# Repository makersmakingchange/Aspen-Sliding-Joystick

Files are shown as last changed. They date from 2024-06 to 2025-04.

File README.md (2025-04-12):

# Aspen Sliding Joystick
The Aspen Sliding Joystick is a small, proportional joystick that has a sliding motion and can be used for adaptive gaming or computer access with a suitable adapter. It has a small range of motion of ±2mm and requires approximately 115 grams-force to fully deflect. It is low profile, with a height of 1.9 cm with the standard topper. This joystick has interchangeable toppers, an optional hand support, and optional mount adapters. The Aspen Sliding Joystick has the same joystick mechanism as the Birch Sliding USB Joystick, but is the analog version. 

The Aspen Joystick has a cable with a 3.5 mm TRRS audio plug (i.e., headphone jack). It is compatible with the [Forest Joystick Mouse Hub](https://www.makersmakingchange.com/s/product/forest-joystick-mouse-hub/01tJR000000E4bdYAC), the Sony PlayStation Access Controller, or the X1 or X2 analog input ports on the Microsoft Xbox Adaptive controller.

The device is comprised of off-the-shelf electronics and 3D-printed parts. The overall cost of materials for a single build is about $20 ($12 for the materials and $8 for shipping).

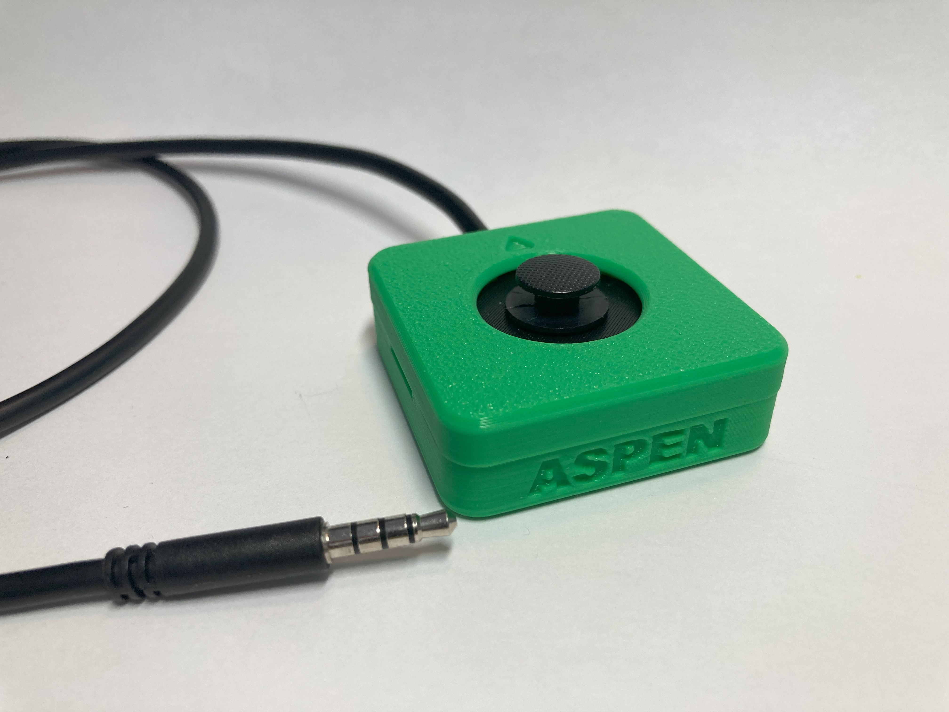
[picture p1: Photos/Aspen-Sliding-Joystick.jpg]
Picture of the Aspen Sliding Joystick, it is small and green and has ASPEN written on the front. The black cable comes out the back of the joystick and wraps around to show the jack on the end.


The Aspen Sliding Joystick can also be used with optional mount adapters to allow for use with a 1/4-20" camera mount or RAM mount systems. There is also an optional 3D-printed hand support. Below, pictured from left to  right are the Camera Mount Adapter, the RAM B Mount Adapter, and the Aspen Hand Support. 

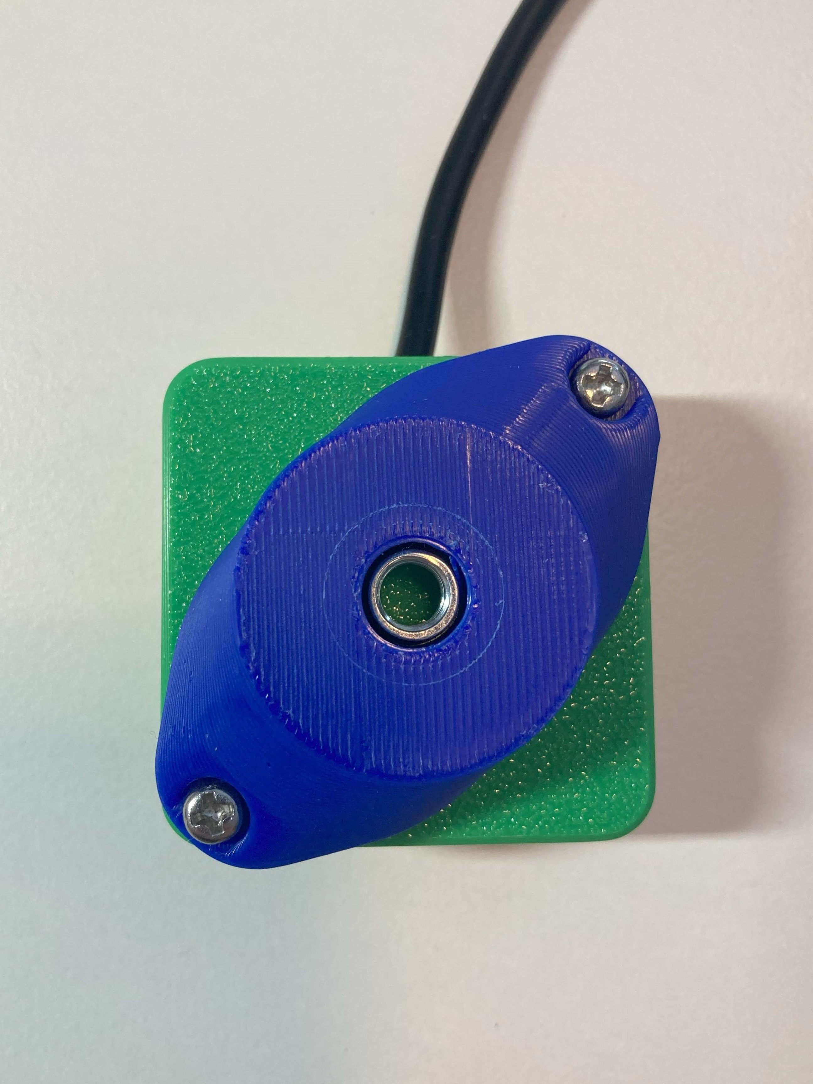
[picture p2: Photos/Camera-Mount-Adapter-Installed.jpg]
Picture of the back of a green Aspen Sliding Joystick with a blue camera mount adapter screwed into it. A black cable comes out the back of the joystick and goes out of frame.
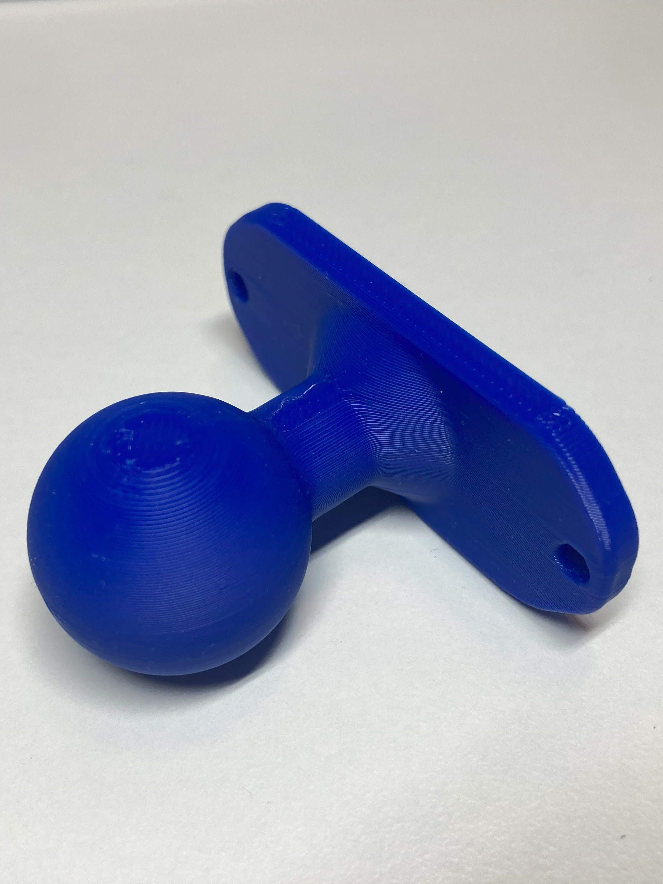
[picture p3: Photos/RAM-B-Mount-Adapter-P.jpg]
Picture of a blue RAM B mount adapter on a white background.
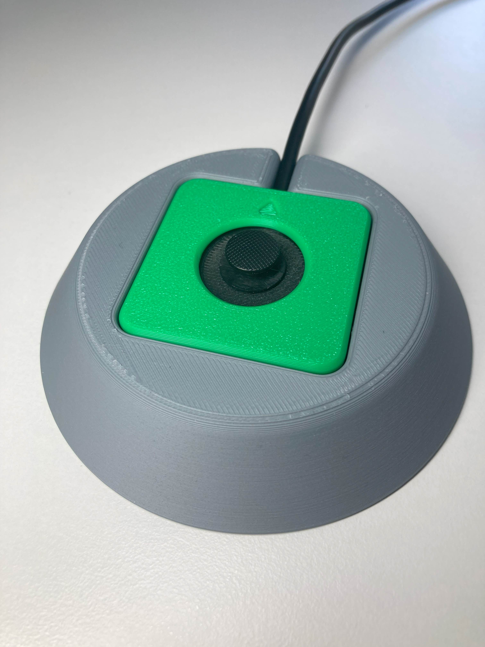
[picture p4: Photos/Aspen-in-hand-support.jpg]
Picture of a green Aspen Sliding Joystick in a grey circular hand support.A black cable comes out the back of the joystick and goes out of frame.
  

## More info at
- [Makers Making Change Assistive Device Library Listing](https://www.makersmakingchange.com/s/product/aspen-sliding-joystick/01tJR000004sCptYAE)

## OpenAT Joysticks
This design is part of the [OpenAT Joystick Project](https://github.com/makersmakingchange/OpenAT-Joysticks), a collection of open source designs for digital access and adapted gaming.  

## How to Obtain a Aspen Sliding Joystick
### 1. Do it Yourself (DIY) or Do it Together (DIT)

This is an open-source assistive technology, so anyone is free to build it. All of the files and instructions required to build the Aspen Sliding Joystick are contained within this repository. Refer to the Maker Guide below.

### 2. Request a build of this device

If you would like to obtain an Aspen Sliding Joystick, you may submit a build request through the [MMC Library Page](https://www.makersmakingchange.com/s/product/aspen-sliding-joystick/01tJR000004sCptYAE). The requestor is responsible for the cost of materials and any shipping.

### 3. How to build this device for someone else

If you have the skills and equipment to build this device, and would like to donate your time to create the joystick for someone who needs it, visit the [MMC Maker Wanted](https://makersmakingchange.com/maker-wanted/) section.

## Getting Started

### 1. Verify Joystick Type
The Aspen Sliding Joystick is an analog joystick that uses a [TRRS](https://www.sparkfun.com/products/11580) lead to connect to an existing gamepad such as the [Forest Joystick Mouse Hub](https://www.makersmakingchange.com/s/product/forest-joystick-mouse-hub/01tJR000000E4bdYAC), the Microsoft Xbox Adaptive Controller (XAC), or the Sony PlayStation Access Controller. Verify that this is the type of joystick the user would like. 

If they want a USB joystick with the same sliding motion instead, they should be directed to the Birch Sliding USB Joystick.

<!---
Other available joysticks can be found through the [Joystick Selection Guide](https://makersmakingchange.com/resource/analog-joystick-selection-guide/)
--->

### 2. Read through the Maker Guide

The [Maker Guide](/Documentation/Aspen_Joystick_Maker_Guide.pdf) contains all the necessary information to build the device.

### 3. Read the Makers Checklist

Use the Makers Checklist in the [Maker Guide](/Documentation/Aspen_Joystick_Maker_Guide.pdf) to confirm details and customization options with the user.

### 4. Order the Off-The-Shelf Components

The [Bill of Materials](/Documentation/Aspen_Joystick_BOM.csv) lists all of the parts and components required to build the Aspen Sliding Joystick. 

### 5. Print the 3D Printable components

Print the components needed for the Aspen Sliding Joystick. Make sure to ask the user if they would like any of the optional prints such as toppers, mount adapters, or the hand support. 

All of the files and individual print files can be in the [/Build_Files/3D_Print_Files](/Build_Files/3D_Print_Files/) folder.

### 6. Assemble the Aspen Sliding Joystick

Reference the Assembly Guide section in the [Maker Guide](/Documentation/Aspen_Joystick_Maker_Guide.pdf) for the tools and steps required to build the device.

## Files
### Documentation
| Document             | Version | Link 	| 
|----------------------|---------|------------------------------------------------------------------------------------------|
| Design Rationale     | 1.0     | [Aspen_Joystick_Design_Rationale](/Documentation/Aspen_Joystick_Design_Rationale.pdf)    |
| Maker Checklist      | 1.0     | [Aspen_Joystick_Maker_Guide](/Documentation/Aspen_Joystick_Maker_Guide.pdf)           	| 
| Bill of Materials    | 1.0     | [Aspen_Joystick_Bill_of_Materials](/Documentation/Aspen_Joystick_BOM.csv)     		    |     
| User Guide           | 1.0     | [Aspen_Joystick_User_Guide](/Documentation/Aspen_Joystick_User_Guide.pdf)    	        | 
| Changelog            | 1.0     | [CHANGES](/CHANGES.txt)     			| 

### Design Files
 - [CAD Files](/Design_Files)

### Build Files
 - [3D Print Files](/Build_Files/3D_Print_Files)

## License

Everything needed or used to design, make, test, or prepare the Aspen Sliding Joystick is licensed under the CERN 2.0 Weakly Reciprocal license <https://ohwr.org/project/cernohl/wikis/Documents/CERN-OHL-version-2> (CERN-OHL-W).

Accompanying material such as instruction manuals, videos, and other copyrightable works that are useful but not necessary to design, make, test, or prepare the Aspen Sliding Joystick are published under a Creative Commons Attribution-ShareAlike 4.0 license <https://creativecommons.org/licenses/by-sa/4.0/> (CC BY-SA 4.0).

## Attribution

Contributors
- Josie Versloot, Neil Squire. Design and documentation. 

The documentation template was created by Makers Making Change / Neil Squire and is used under a CC BY-SA 4.0 license. It is available at the following link: https://github.com/makersmakingchange/OpenAT-Template

---

<!-- ABOUT MMC START -->
## About Makers Making Change
[Makers Making Change Logo](https://www.makersmakingchange.com/)

Makers Making Change is a program of [Neil Squire](https://www.neilsquire.ca/), a Canadian non-profit that uses technology, knowledge, and passion to empower people with disabilities.

Makers Making Change leverages the capacity of community based Makers, Disability Professionals and Volunteers to develop and deliver affordable Open Source Assistive Technologies.

 - Website: [www.MakersMakingChange.com](https://www.makersmakingchange.com/)
 - GitHub: [makersmakingchange](https://github.com/makersmakingchange)
 - Bluesky: [@makersmakingchange.bsky.social](https://bsky.app/profile/makersmakingchange.bsky.social)
 - Instagram: [@makersmakingchange](https://www.instagram.com/makersmakingchange)
 - Facebook: [makersmakechange](https://www.facebook.com/makersmakechange)
 - LinkedIn: [Neil Squire Society](https://www.linkedin.com/company/neil-squire-society/)
 - Thingiverse: [makersmakingchange](https://www.thingiverse.com/makersmakingchange/about)
 - Printables: [MakersMakingChange](https://www.printables.com/@MakersMakingChange)

### Contact Us
For technical questions, to get involved, or to share your experience we encourage you to [visit our website](https://www.makersmakingchange.com/) or [contact us](https://www.makersmakingchange.com/s/contact).
<!-- ABOUT MMC END -->

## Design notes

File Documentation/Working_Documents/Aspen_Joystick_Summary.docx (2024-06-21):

This document is intended to be a summary of a device to make it easier to add to the website.

# Product Information

## Product Name

Aspen Sliding Joystick

## Device Category

Mark any relevant categories with an “X”:

| Adapted Toys
| Aids for Daily Living (ADL)
| Assistive Switches
| Communication Aids (AAC)
X | Computer Access
| Environmental Controls
X | Gaming
| Keyguard
| Kits
| LipSyncs
| Mounting
X | Recreation and Leisure
| Seating and Positioning
| Switch Interfaces
| Writing Aids

## User Value Statement

If you're looking for a small, analog joystick with a very small range of motion we'd like to point you to the Aspen Sliding Joystick.

## Designer

Makers Making Change

# Device Info

## Overview

The Aspen Sliding Joystick is a small analog joystick that moves in a sliding motion instead of the typical pivoting motion of a joystick or thumbstick. It can be used for adapted gaming or computer access with a suitable adaptive controller or hub. This joystick can be used directly with the Xbox Adaptive Controller (https://www.xbox.com/en-CA/accessories/controllers/xbox-adaptive-controller) or PlayStation Access Controller, or can be combined with the Forest Joystick Mouse Hub (https://github.com/makersmakingchange/Forest-Joystick-Mouse-Hub) and some assistive switches to create a USB HID Mouse or USB HID Gamepad.

The PSP-style game controller sliding thumbstick joystick has a range of motion of ±2 mm and requires approximately 115 grams-force to fully deflect. A range of toppers and mounting adapters are available for this joystick. The Aspen Sliding Joystick has the same joystick mechanism as the Birch Sliding USB Joystick, but is the analog version.

## Disability Type

Select one or more disability types and mark with an “X”:

X | Agility / Dexterity
| Arthritis
| Cognitive
| Hearing
| Mobility
| Mobility
| Pain
X | SCI
| Vision
| Other

## Disability Type Description

This device is designed for users with a very small range of motion that need an external joystick for adaptive gaming or computer access.

## How To Use

To use the Aspen Sliding USB Joystick, first position the joystick for the user, mounting if needed. Then, plug in the 3.5 mm cable to the host device, such as the Forest Hub, Xbox Adaptive Controller, or PlayStation Access Controller.

For full instructions, please refer to the User Guide (https://github.com/makersmakingchange/Aspen-Sliding-Joystick/blob/main/Documentation/Aspen_Joystick_User_Guide.pdf).

## Estimated Cost

The estimated material cost of the device for a single build:

| $0 - $10
X | $11 - $25
| $26 - $50
| $51 - $100
| $101 - $250
| $250+

## Attribution

Designed by Neil Squire Society / Makers Making Change

Contributors

- Josie Versloot, Neil Squire. Design and documentation.

The documentation template was created by Makers Making Change / Neil Squire and is used under a CC BY-SA 4.0 license. It is available at the following link: https://github.com/makersmakingchange/OpenAT-Template

# Maker Info

## Project Skills

Mark the required project skills with an “X”:

X | 3D Printing
| Custom PCB
| Electronics
| Laser Cutting
| Mechanics
| Software
X | Soldering
| Woodworking
| Other

## Skills Description

This is an intermediate build requiring 3D printing, and soldering electronic components.

## Tools Needed

X | 3D Printer
X | Common Hand Tools
| Common Power Tools
| Laser Cutter
X | Soldering Iron
| Specialized Tooling

## Print time (hrs)

1.5

## Assembly time (hrs)

1.0

## Build Instructions

This build consists of 4 off the shelf components and a 3D printed enclosure. The commercial parts are soldered together and then assembled into the 3D printed enclosure using snap fits.

Detailed step-by-step instructions are available in the Maker Guide (https://github.com/makersmakingchange/Aspen-Sliding-Joystick/blob/main/Documentation/Aspen_Joystick_Maker_Guide.pdf).

## Download Link

https://github.com/makersmakingchange/Aspen-Sliding-Joystick/archive/refs/heads/main.zip

## Project Link

https://github.com/makersmakingchange/Aspen-Sliding-Joystick

# License

## License

This repository describes Open Hardware:

- Everything needed or used to design, make, test, or prepare the Aspen Sliding Joystick is licensed under the CERN 2.0 Weakly Reciprocal license (CERN-OHL-W v2) or later (https://cern.ch/cern-ohl) .
- Accompanying material such as instruction manuals, videos, and other copyrightable works that are useful but not necessary to design, make, test, or prepare the Aspen Sliding Joystick are published under a Creative Commons Attribution-ShareAlike 4.0 license (CC BY-SA 4.0) (https://creativecommons.org/licenses/by-sa/4.0/) .

You may redistribute and modify this documentation and make products using it under the terms of the CERN-OHL-W v2 (https://cern.ch/cern-ohl). This documentation is distributed WITHOUT ANY EXPRESS OR IMPLIED WARRANTY, INCLUDING OF MERCHANTABILITY, SATISFACTORY QUALITY AND FITNESS FOR A PARTICULAR PURPOSE. Please see the CERN-OHL-W v2 for applicable conditions.

© 2024 by Neil Squire. This work is licensed under the CC BY SA 4.0 License: http://creativecommons.org/licenses/by-sa/4.0 Page 1 of 2

V1.0 | JUNE 2024 Aspen Sliding Joystick Summary

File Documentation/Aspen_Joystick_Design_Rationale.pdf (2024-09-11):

V1.1 | SEPTEMBER 2024

## Aspen Sliding Joystick

## DESIGN RATIONALE

© 2024 by Neil Squire Society. (https://www.neilsquire.ca/)

This work is licensed under the CC BY SA 4.0 License: http://creativecommons.org/licenses/by-sa/4.0
Files available at https://github.com/makersmakingchange/Aspen-Sliding-Joystick | Page 1 of 23

### Introduction

With adaptive gaming joysticks that are compatible with both PC and XAC being difficult to source globally, MMC aims to provide a cost-effective, open source customizable joysticks using easy to source components. Unlike commercial versions, these devices will be designed for Maker assembly with all the digital files necessary to customize key components easily.

The Aspen Sliding Joystick is the smaller, analog, version of the Birch Sliding Joystick. Previously, the analog and USB versions of the sliding joystick were made using the same enclosure and were named the Birch Mini Joystick-A and Birch Mini Joystick-U. The analog version was a lot bigger than it needed to be, and hardware increased the cost, so the Aspen Sliding Joystick came to be.

The intended user is someone with a very small range of motion, or for someone who prefers a joystick with a sliding motion.

### Research

### Commercially Available Options

1. Inclusive Inc Slider Joystick (https://inclusiveinc.org/en-ca/products/slider-joystick)

Cost (without shipping): $208.00 CAD

Dimensions: Not given

Features:

- Made to work with Versatilty v3 (https://inclusiveinc.org/products/v3) with circular 8 pin analog joystick port
- Low profile (no dimensions indicated)
- Mounting slots on the side

## DESIGN RATIONALE

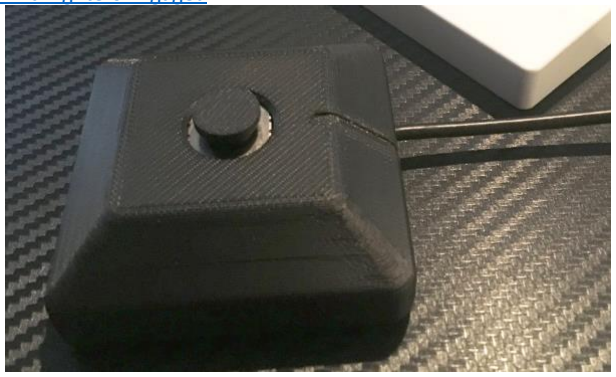
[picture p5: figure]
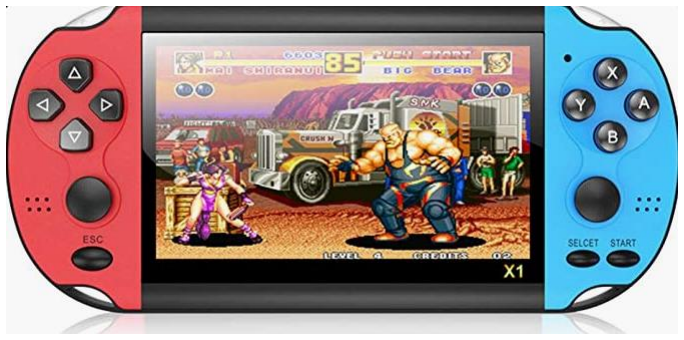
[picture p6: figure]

Files available at https://github.com/makersmakingchange/Aspen-Sliding-Joystick | Page 2 of 23
2. MINISTIX-SL Warfighters Engaged (https://warfighterengaged.org/shop/ministix-s)

Cost (without shipping): $45.00 USD

Dimensions: Not given

Features:

- ¼-20 threaded hole on the back for mounting.
- 3.5 mm integrated cable
3. Amazon - PSP type device (https://www.amazon.ca/ZADAI-4-3-inch-Handheld-Console-Portable/dp/B095WXBYSQ?hvadid=582450275413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)
*This example is more of how the device has sliding joysticks incorporated as the PlayStation PSP or Vita are no longer available.

Cost (without shipping): $99.99 CAD

Dimensions: N/A

## DESIGN RATIONALE

Files available at https://github.com/makersmakingchange/Aspen-Sliding-Joystick | Page 3 of 23

Features:

- Uses two sliding joysticks in a handheld set up for two handed gaming.
- Replaces the PlayStation PSP and Vita which popularized sliding joysticks in gaming

### Open Source Options:

1. Slider Joystick MKIII - Ron Nelson (https://www.etsy.com/ca/listing/1191918398/slider-joystick-mkiii-for-xbox-adaptive?click_sum=caf10b44&crt=1)
a. Github: https://github.com/nelsonii/JoystickEnclosures/tree/main/Slider

Cost (without shipping):

- Sold for: $77.86 CAD
Dimensions: N/A

Features:

- USB connection (intended for XAC)
- LED indicator light
- PC compatibility and also used with JoyToKEy (https://joytokey.net/en/)
- Features 3D printed disk topper with rubber 1.5 inch inserts for increased surface area

## DESIGN RATIONALE

Files available at https://github.com/makersmakingchange/Aspen-Sliding-Joystick | Page 4 of 23

### Requirements

### Goals

G01 | Minimize the size of the enclosure.
G02 | Minimize the cost.

### Functional Requirements

F01 | The joystick design must have a 3.5 mm TRRS analog output.
F02 | The joystick must be compatible with the Xbox Adaptive Controller and Forest Hub.
F03 | The joystick shall be designed to be used by either hand.
F04 | Joystick must remain stable while in use.
F05 | Joystick design must reduce possibilities of damage to electronic components of device by reducing openings to internal components.

### Constraints

C01 | Joystick must be maker manufacturable. (i.e. made with common tools and materials)
C02 | Design must be considered low profile and the total height must not exceed that of the Birch Mini Joystick, which is 24 mm.
C03 | The total maker cost must be less than or equal to that of the Birch Mini Joystick-A, which was $38.76.
C04 | The joystick must include two M3 nuts 50 mm apart to be compatible with the Joystick Mount Adapters.

## DESIGN RATIONALE

Files available at https://github.com/makersmakingchange/Aspen-Sliding-Joystick | Page 5 of 23

### Ideation

### Key Features

Joystick Unit
For this design, the same joystick element will be used as the Birch Joystick, the small sliding thumbstick from Adafruit. It is called the “Mini 2-Axis Analog Thumbstick” on the Adafruit website, product number 2765.

Snap fit to secure joystick
In this design, one of the goals was to minimize the cost, and decrease the cost compared to the Birch Mini Joystick-A design. One of the main costs when doing a single build of this previous design was fasteners, the M2 screws needed to fit through the joystick breakout board were difficult to find in small quantities and had to be bought in a pack of 1000. To eliminate this, a snap fit would be explored to secure the joystick.

Snap fit enclosure
To further reduce costs, a snap fit enclosure will also be explored, in the aim to eliminate the cost of fasteners altogether.

Mounting
To allow for different mounting options, captive M3 nuts compatible with the OpenAT Joystick Mount Adapters will be included. These must be 50 mm apart, and will allow different mount adapters to be attached to the bottom of the joystick, including a ¼-20” camera mount.

### Conceptual Design

The size of the joystick unit is quite small, and therefore the required dimensions of the captive nuts for the mount adapter will be the main constraint when it comes to size. There are two main ways the captive nuts can be oriented, vertically, horizontally, or diagonally. To allow users to place other devices close to the joystick, the vertical orientation is preferred over horizontal, so the vertical and diagonal mount adapter options were explored further.

### Concept 1 : Vertical Mount Adapter

With the mount adapter nuts in a vertical orientation, this creates a very long and skinny joystick when trying to minimize size. For aesthetics and stability, more width could be added to this design if needed. The dimensions of this concept would be approximately 35 mm x 60 mm at this minimum size.

## DESIGN RATIONALE

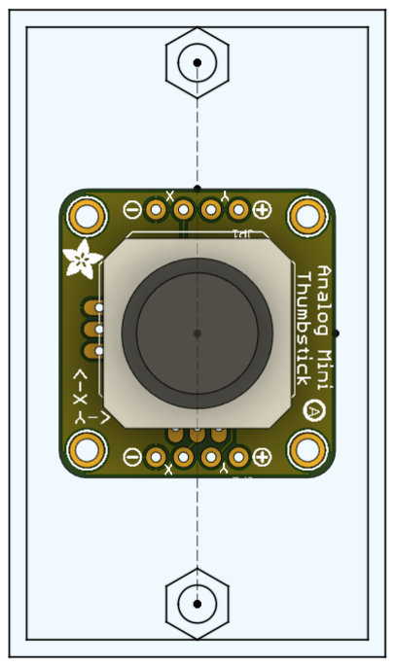
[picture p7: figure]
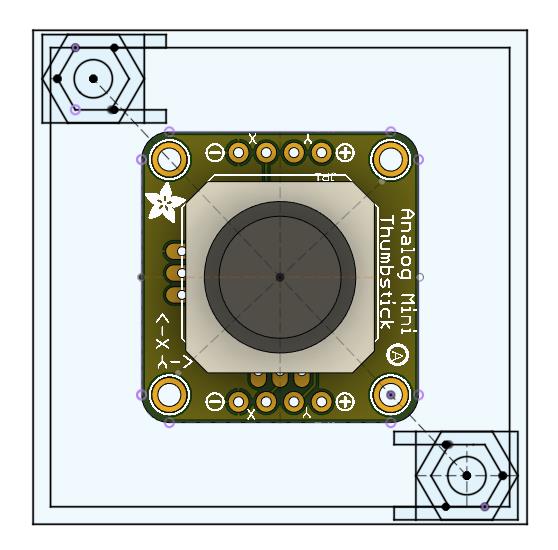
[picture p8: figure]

Files available at https://github.com/makersmakingchange/Aspen-Sliding-Joystick | Page 6 of 23

### Concept 2 : Diagonal Mount Adapter

With the mount adapter nuts in a diagonal orientation, the joystick would be more square. At these minimum dimensions, the size of this concept would be around 45 mm x 45 mm.

### Concept Selection

The concept with the diagonal mount adapter nuts was chosen, due to its more square geometry, which would be more stable while in use, is more aesthetically pleasing, and has a smaller overall footprint.

## DESIGN RATIONALE

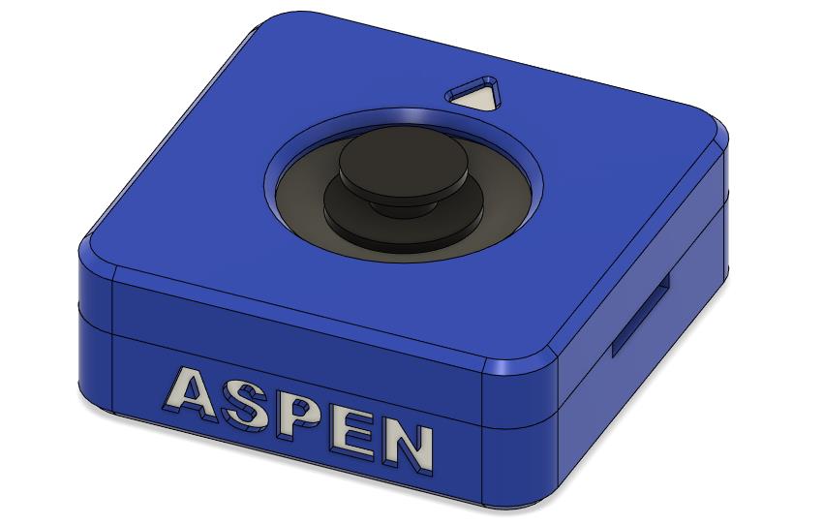
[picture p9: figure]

Files available at https://github.com/makersmakingchange/Aspen-Sliding-Joystick | Page 7 of 23

### Detailed Design

### Overview

The Aspen Sliding Joystick is small and compact, with a snap fit enclosure. Below the overall design is pictured:

Components
The components used in this design are the sliding joystick module and breakout board, a TRRS stereo audio cable, and 2 hex nuts. The parts are all listed in the following table, and more information including prices can be found in the Bill Of Materials (BOM).
Part Name | QTY | Link
Mini 2-Axis Analog Thumbstick | 1 | https://www.digikey.ca/en/products/detail/adafruit-industries-llc/2765/6193582 (https://www.digikey.ca/en/products/detail/adafruit-industries-llc/2765/6193582)
Analog Mini Thumbstick Breakout Board | 1 | https://www.digikey.ca/en/products/detail/adafruit-industries-llc/3246/6193594 (https://www.digikey.ca/en/products/detail/adafruit-industries-llc/3246/6193594)
3.5 mm stereo cable (4 conductor, TRRS, M-M) | 1 | https://www.digikey.ca/en/products/detail/tensility-international-corp/10-00332/2350238 (https://www.digikey.ca/en/products/detail/tensility-international-corp/10-00332/2350238)
M3 hex nut | 2 | https://www.digikey.ca/en/products/detail/keystone-electronics/4708/4499301 (https://www.digikey.ca/en/products/detail/keystone-electronics/4708/4499301)

## DESIGN RATIONALE

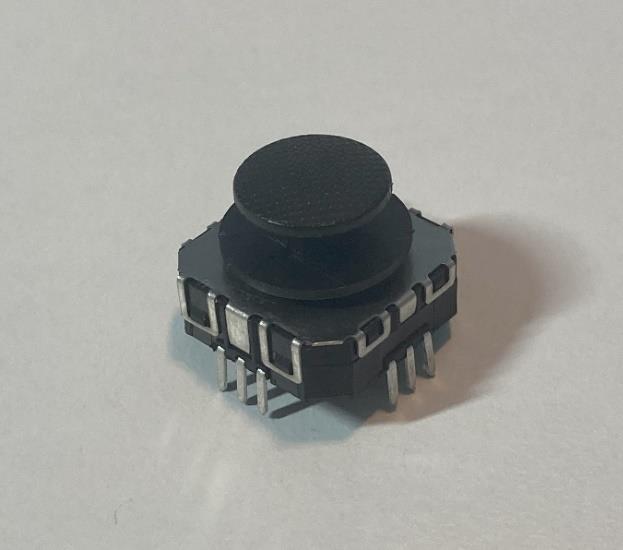
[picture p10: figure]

Files available at https://github.com/makersmakingchange/Aspen-Sliding-Joystick | Page 8 of 23

The Aspen Joystick was designed around this thumbstick module listed above and pictured here:

The other key component is the joystick breakout board listen above and pictured here:

## DESIGN RATIONALE

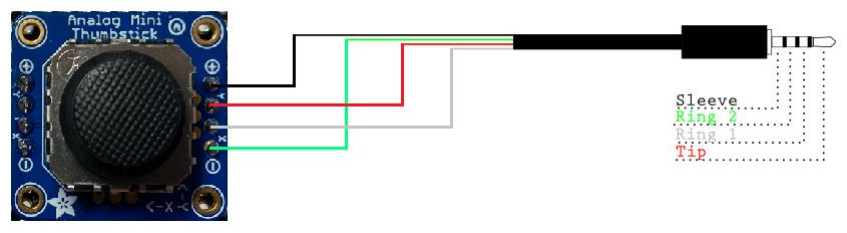
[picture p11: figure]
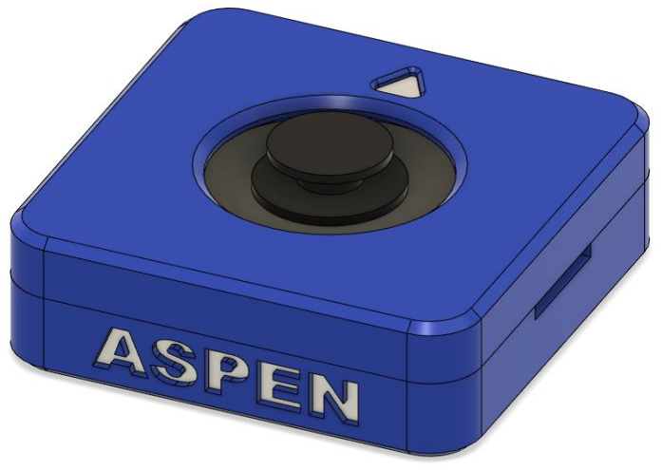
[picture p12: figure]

Files available at https://github.com/makersmakingchange/Aspen-Sliding-Joystick | Page 9 of 23

### Electronics Design

Wiring Diagram
The following photo and table show how the joystick is wired to the TRRS cable.

Figure 1. Joystick Wiring Guide. Image Remixed from Sparkfun, released under a CC BY 2.0 license.

Table 1: Aspen Wiring

### Housing Design

Outer features
On the outside of the enclosure there are a few key features. On the side facing the user, “ASPEN” is engraved, and on the side facing away rom the user “MMC” is engraved. There is also an arrow on the top of the enclosure showing the up direction.
Joystick Breakout Board | CONNECTION | Digikey TRRS Cable
+ | Sleeve (S) | Black
Y | Tip (T) | Red
X | Ring 1 (R1) | White
- | Ring 2 (R2) | Green

## DESIGN RATIONALE

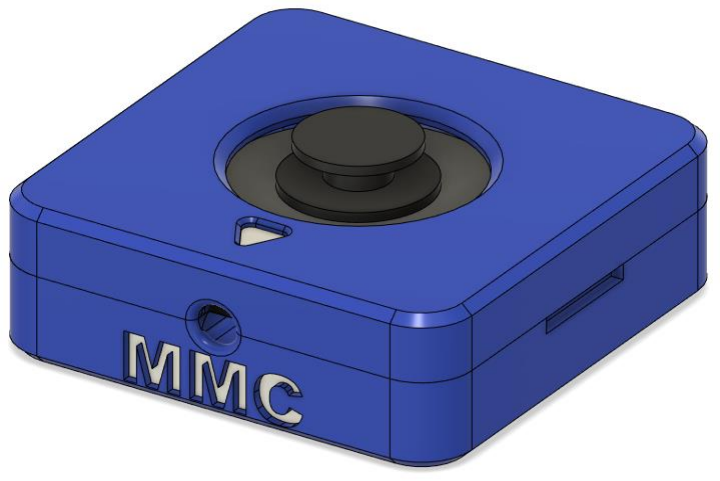
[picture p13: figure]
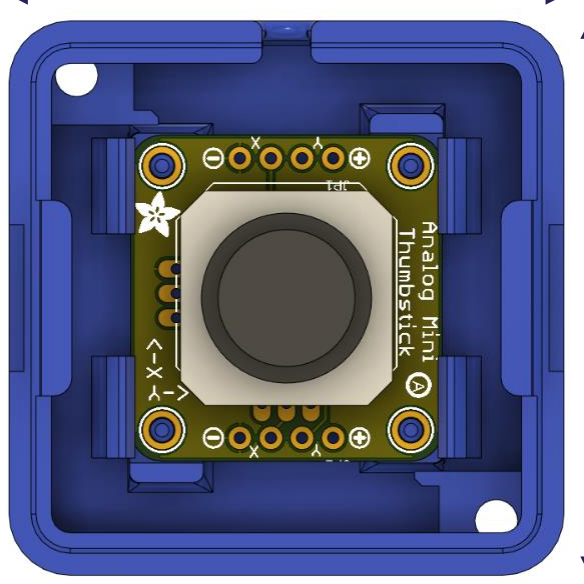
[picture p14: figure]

Files available at https://github.com/makersmakingchange/Aspen-Sliding-Joystick | Page 10 of 23

On the sides of the enclosure there is a small indent, to allow for some leverage when prying apart the snap fit enclosure. On the backside of the enclosure there is a hole for the cable exit.

Housing Footprint
One of the goals with the Aspen Sliding Joystick was to reduce the size compared to the Birch Mini Joystick. Here, the footprint was able to be reduced significantly, only needing room for the joystick breakout board, and enough distance between the captive nuts for the mount adapter. The footprint of the Aspen Sliding Joystick is 45 mm x 45 mm as seen below:

This is a significant size reduction compared to the previous design, the Birch Mini Joystick, which had a footprint of 60 mm x 68 mm, shown below.

45mm

45mm

## DESIGN RATIONALE

Files available at https://github.com/makersmakingchange/Aspen-Sliding-Joystick | Page 11 of 23

Here the two joystick designs are shown side by side to compare:

60mm

68mm

## DESIGN RATIONALE

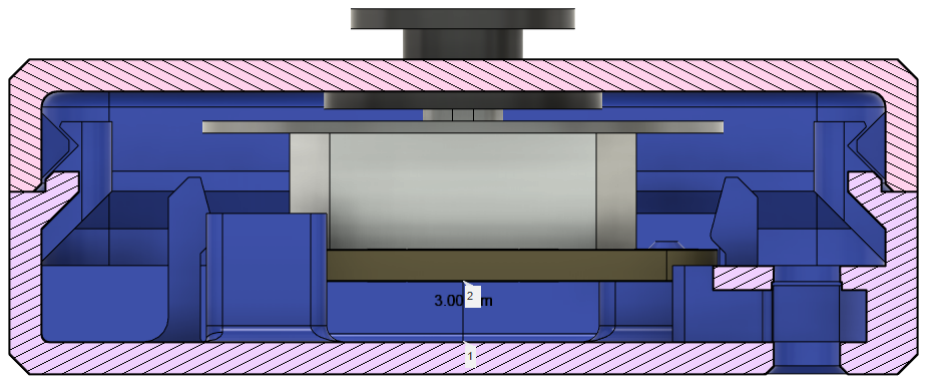
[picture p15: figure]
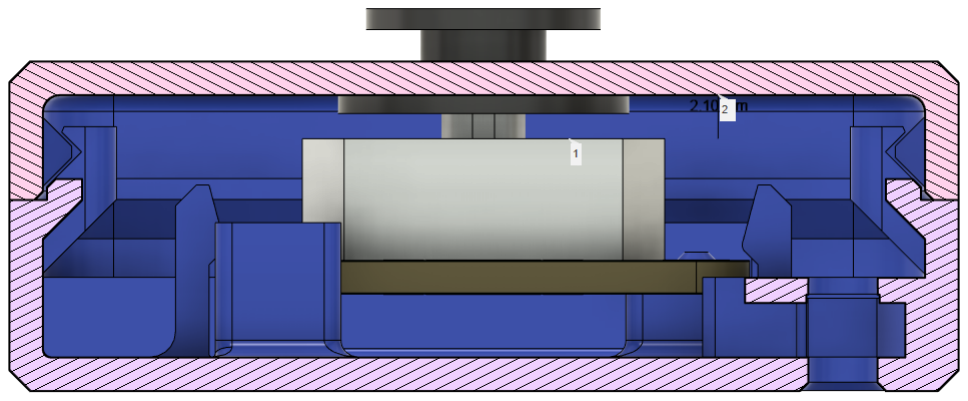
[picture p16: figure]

Files available at https://github.com/makersmakingchange/Aspen-Sliding-Joystick | Page 12 of 23

Housing Height
The overall height of the joystick housing is 15.7 mm. Some key measurements here are the distance below the joystick breakout board, to allow for clearance of the wires after soldering, and the distance between the top of the joystick and the top of the enclosure.

The distance between the bottom of the joystick breakout board and the bottom of the enclosure is 3 mm and can be seen here:

The distance between the top of the joystick unit and the top of the enclosure is 2.1 mm to allow for the 0.6 mm inner disk and space for smooth sliding between all of these parts, while considering the imperfections of 3D printing, and how not all parts will be fully flush in reality.

## DESIGN RATIONALE

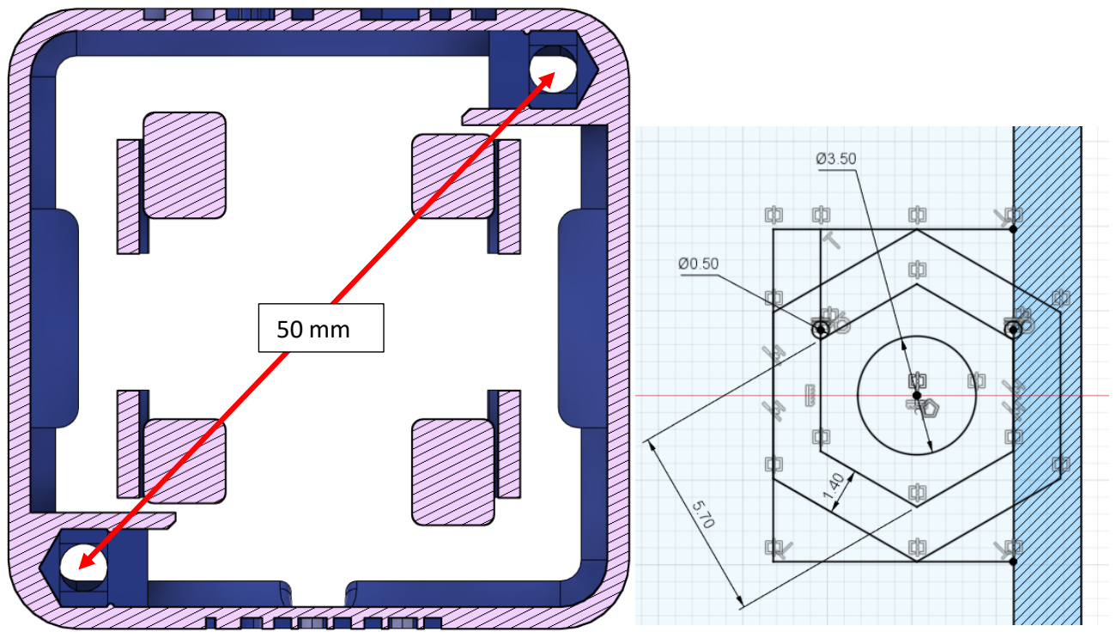
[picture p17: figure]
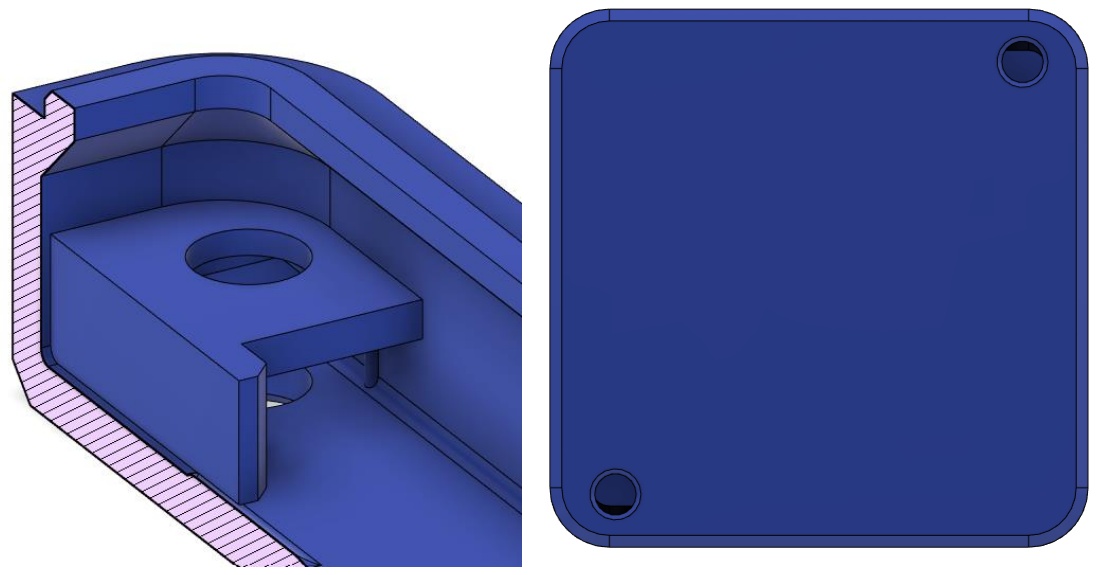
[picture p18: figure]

Files available at https://github.com/makersmakingchange/Aspen-Sliding-Joystick | Page 13 of 23

Mount Adapter Captive Nuts
Like the other OpenAT Joystick designs, the Aspen joystick needed to include captive nuts compatible with the OpenAT Mount Adapters, to allow mounting options when not used on a tabletop. The mount adapters use M3 nuts and screws, with the centres of these nuts are 50.0 mm apart. In this design, the mount adapter will attach diagonally. These two slots are seen in the photos below. As seen in the photo, around the hole above the captive nut, which would be printed unsupported, there are small single layer rectangles, this is a best practice when 3D printing unsupported holes. (https://www.hydraresearch3d.com/design-rules#unsupported-holes)

## DESIGN RATIONALE

Files available at https://github.com/makersmakingchange/Aspen-Sliding-Joystick | Page 14 of 23

Joystick Snap Fit
To hold the joystick breakout board in place, a snap fit and 4 pegs were used to secure it to the bottom of the enclosure. The 4 pegs ensure the joystick stays in position front to back and side to side, while the snap fit ensures that the joystick doesn’t move up and down or come out of the enclosure. Both the snap fit and the pegs can be seen in the cut out view below. The geometry of the snapfit is also shown with some of the key measurements.

The posts are all 0.965 mm in diameter to allow the joystick to fit on snugly, and the distance between the posts is 20.32 mm x 21.59 mm. This can be seen in the photo below.

## DESIGN RATIONALE

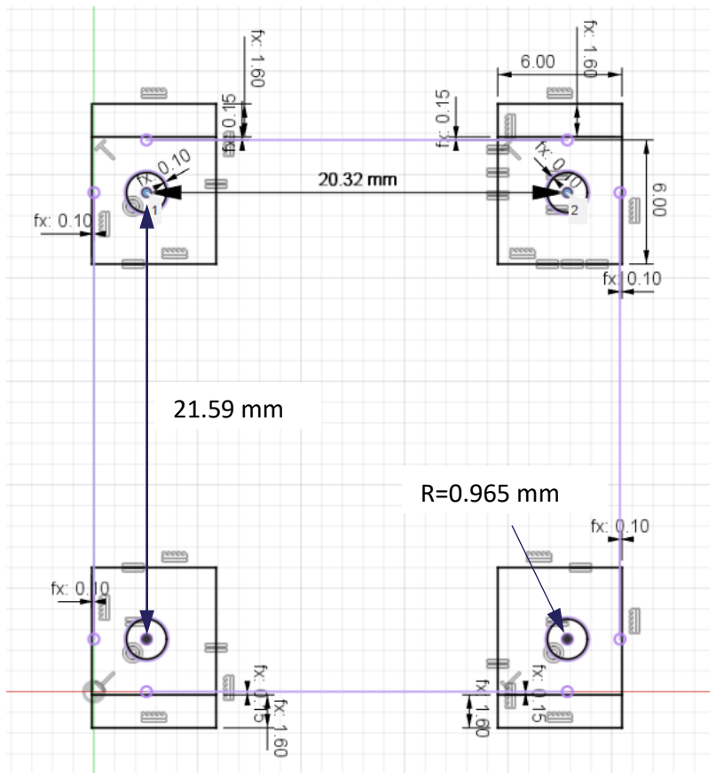
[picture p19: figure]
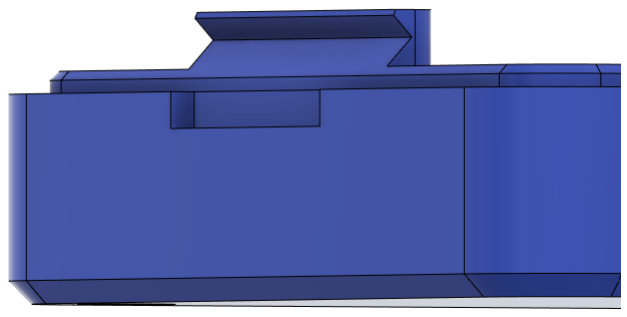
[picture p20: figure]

Files available at https://github.com/makersmakingchange/Aspen-Sliding-Joystick | Page 15 of 23

Housing Snap Fit
To secure the housing together, a snap fit was used. This was to eliminate the need for screws, and therefore reduce the cost of the device.

On the bottom of the enclosure, a piece sticks up above the top surface and has a triangle indent for the top piece to snap into:

## DESIGN RATIONALE

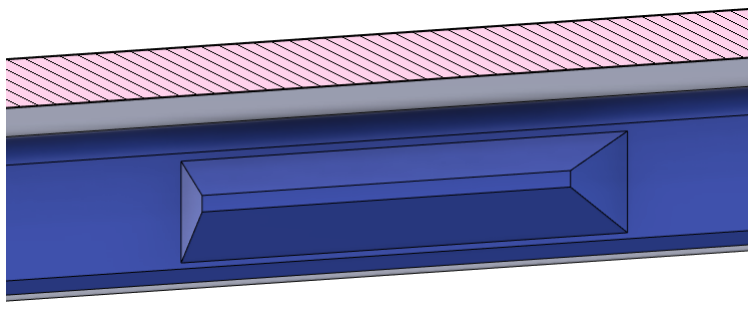
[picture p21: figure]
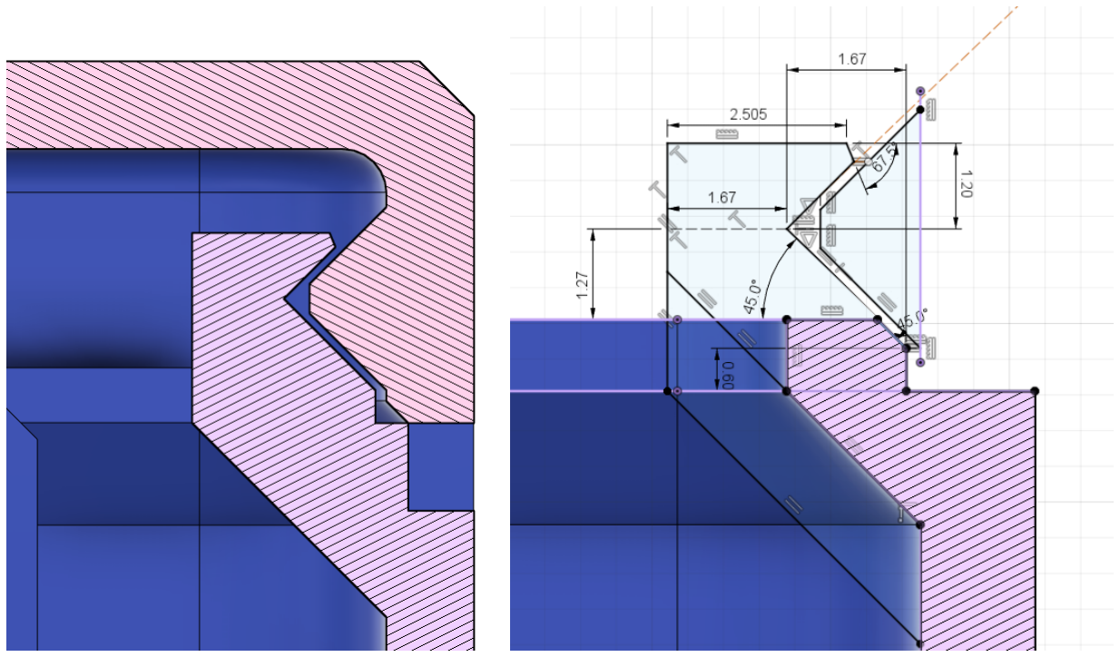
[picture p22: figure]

Files available at https://github.com/makersmakingchange/Aspen-Sliding-Joystick | Page 16 of 23

On the top of the enclosure there is a triangular piece that sticks out to fit into the bottom the the enclosure, along with some fillets and drafts:

In the following section view it can be seen how the pieces fit together as well as some of the geometries and measurements:

Inner Disk
To protect the inner electronics of the joystick, a small disk was added between the sliding joystick component and the topper. The photos below show how the disk is added to the joystick by removing the topper. The disk is 0.6 mm thick so it is thin but still has structural integrity by being three print layers thick. This disk does not need to be strong as there will be no bending force applied to it. It is

## DESIGN RATIONALE

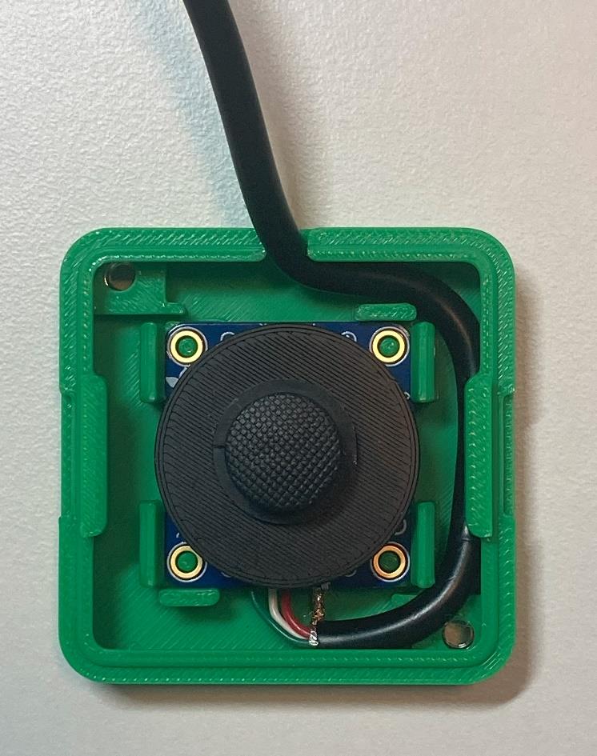
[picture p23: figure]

Files available at https://github.com/makersmakingchange/Aspen-Sliding-Joystick | Page 17 of 23

important to look at the quality of this print, and if there are any bumps or zits, to either cut these off with a craft knife or use sandpaper to create a smooth surface and prevent binding.

Cable Routing
In this joystick design, the TRRS cable is routed around the outside edge inside the enclosure. Since the cable is relatively snug going around the corners, this also provides enough tension relief that if you pull on the cable it won’t pull on the soldered connections.

## DESIGN RATIONALE

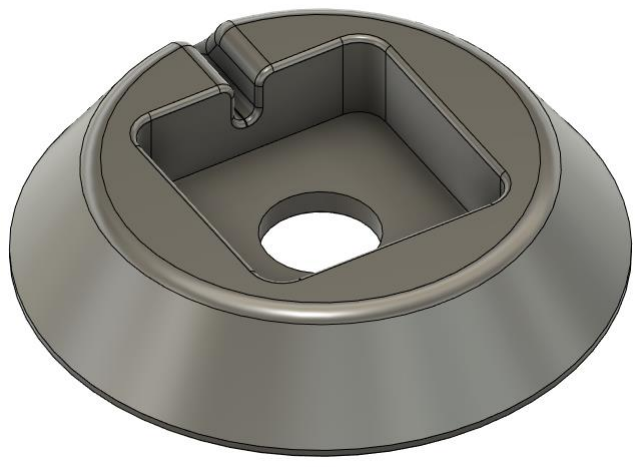
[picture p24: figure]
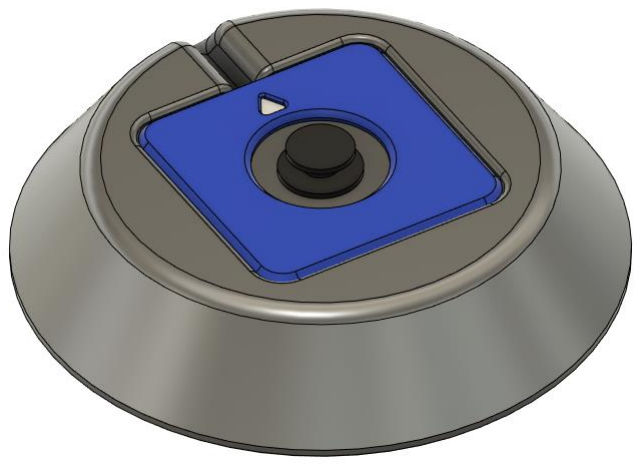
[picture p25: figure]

Files available at https://github.com/makersmakingchange/Aspen-Sliding-Joystick | Page 18 of 23

### Hand Support

Since the Aspen joystick is quite small, we thought some people might prefer a larger joystick enclosure to rest their hand on, so a simple optional hand support was designed that the Aspen could slide into. This support rest would ramp up to the top surface to not dig into the user’s hand, and would increase the footprint of the joystick

Overview
The shape for the hand rest was decided to be circular, so that it could be used in any orientation and to reduce the number of corners that could dig into the user’s hand. There is a cavity for the Aspen joystick to slide into, with a slot out the back for the cable to go through. There is also a hole in the bottom that can be used to push out the joystick to remove it from the hand support.

## DESIGN RATIONALE

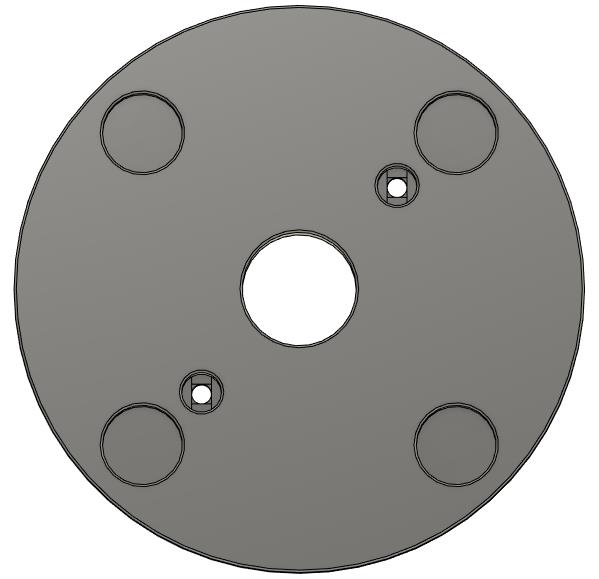
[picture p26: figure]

Files available at https://github.com/makersmakingchange/Aspen-Sliding-Joystick | Page 19 of 23

The bottom circle at the base of the hand support is 100 mm in diameter, and the top circle (at the edge of the top surface) is 75 mm in diameter. This size was used as a starting point but should be tested further to determine an optimal size.

A fillet with a 4 mm diameter was used on the top edge circle so that edges are not digging into the user’s hand.

Indents for non slip pads
On the bottom of the hand support there are 4 circular indents which are intended for optional non slip pads to be added to the bottom of the hand support. The non slip pads that were used to measure the size of these holes have a diameter of 12.5 mm and a height of 3.7 mm. To allow for a variety of non slip pads to be used, the indents in the bottom of the hand rest have a diameter of 14 mm and are 2.4 mm deep (so that they stick out from the bottom still). They are equally spaced near the edge of the circle.

Screw holes
The screw holes in the hand support are designed for the M3 screws that are used for the mounting adapters, compatible with the M3 nuts in the Aspen Joystick. The diameter of the hole is 3.5 mm for a loose sliding fit, and the diameter of the counterbore for the screw head is 7 mm. Best practices for 3D printing unsupported holes were used. (https://www.hydraresearch3d.com/design-rules#unsupported-holes)

## DESIGN RATIONALE

Files available at https://github.com/makersmakingchange/Aspen-Sliding-Joystick | Page 20 of 23

### Assembled Prototype

Below are some photos of the assembled prototype:

## DESIGN RATIONALE

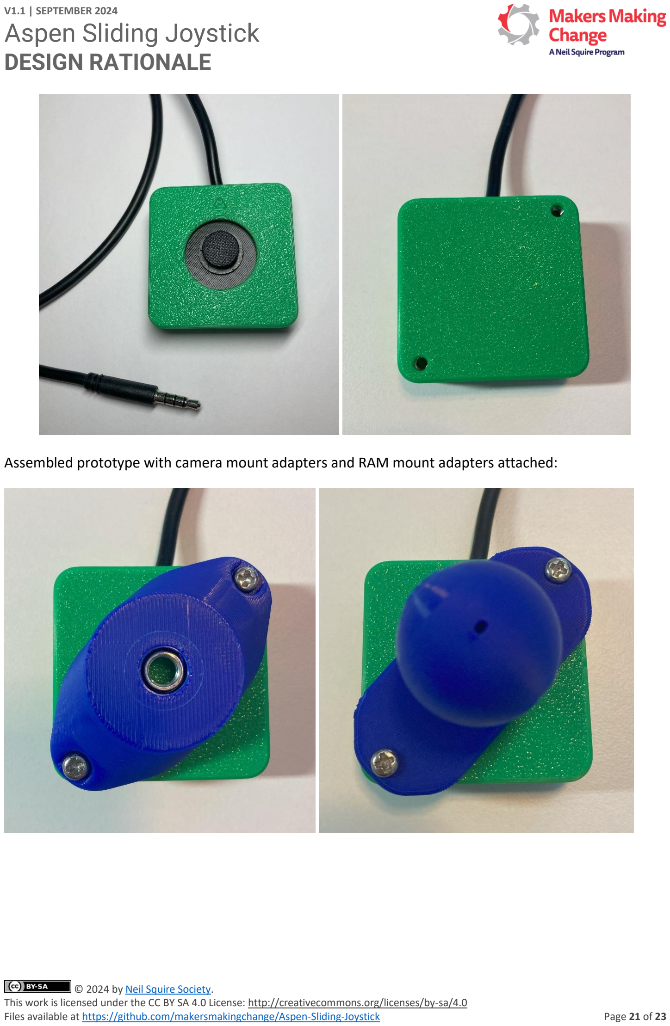
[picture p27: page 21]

Files available at https://github.com/makersmakingchange/Aspen-Sliding-Joystick | Page 21 of 23

Assembled prototype with camera mount adapters and RAM mount adapters attached:

## DESIGN RATIONALE

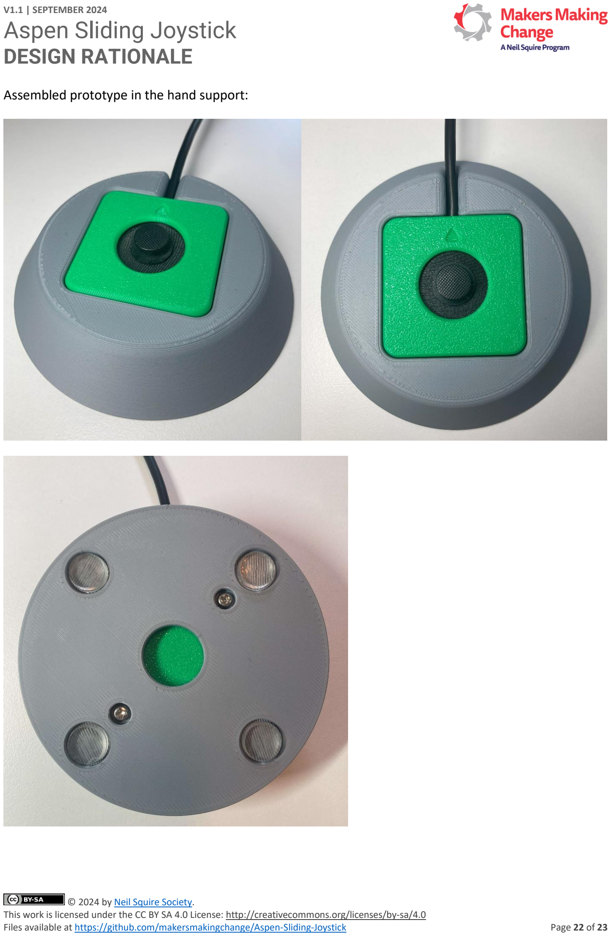
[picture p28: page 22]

Files available at https://github.com/makersmakingchange/Aspen-Sliding-Joystick | Page 22 of 23

Assembled prototype in the hand support:

## DESIGN RATIONALE

Files available at https://github.com/makersmakingchange/Aspen-Sliding-Joystick | Page 23 of 23

### Final Design

### Opportunities for Improvement / Future Work

- Could add a feature to the outside of the enclosure to allow for snap on piece for wrist supports and other bases
- Snap fit could be optimized for a larger variety of printers, on some it is too tight

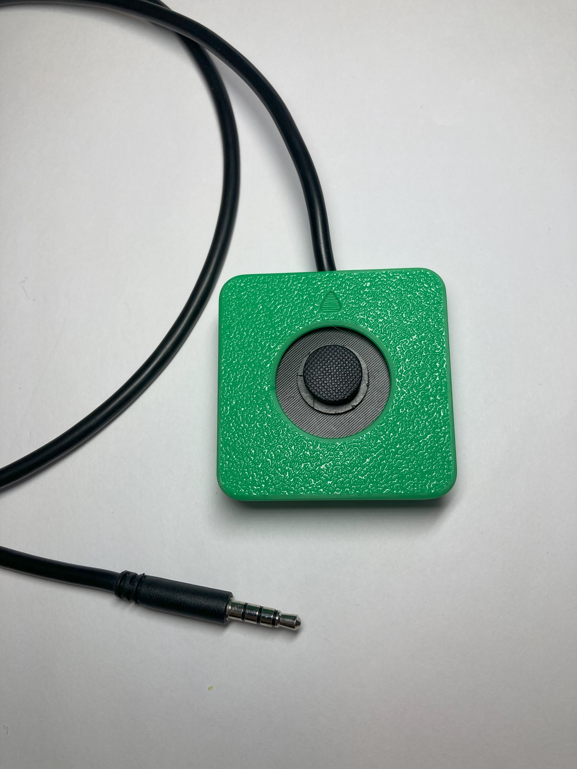
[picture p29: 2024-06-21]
Photos/Aspen-Sliding-Joystick-Above.jpg

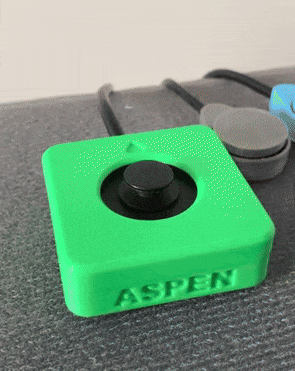
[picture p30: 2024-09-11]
Photos/Aspen-In-Use.gif

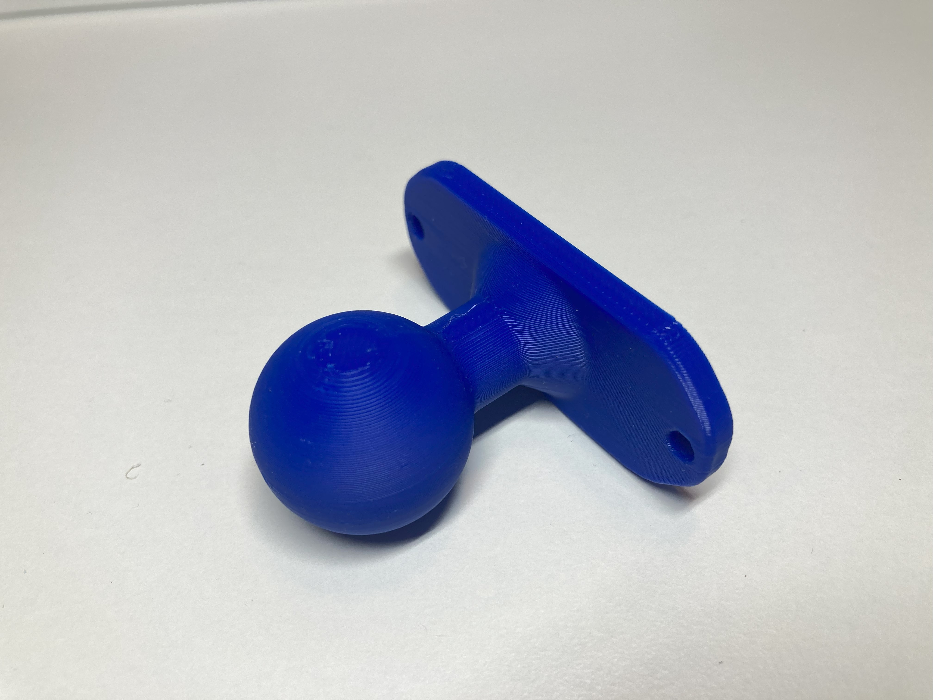
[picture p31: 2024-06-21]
Photos/RAM-B-Mount-Adapter.jpg

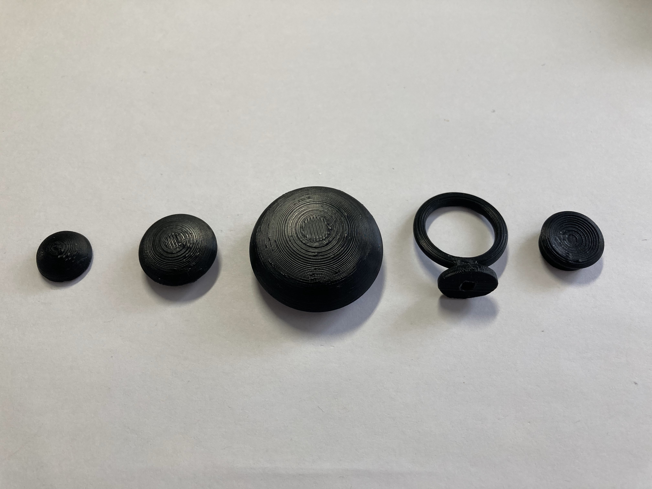
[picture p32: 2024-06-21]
Photos/Sliding-Joystick-Toppers.jpeg

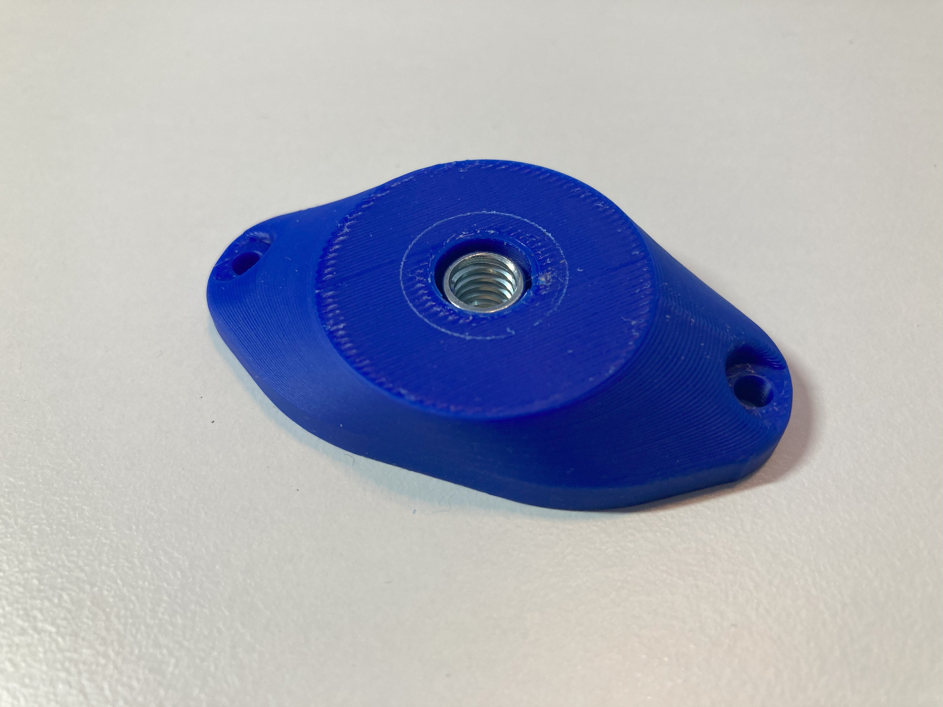
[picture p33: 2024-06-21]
Photos/Camera-Mount-Adapter.jpg

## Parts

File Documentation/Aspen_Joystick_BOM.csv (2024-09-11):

Aspen Sliding Joystick |  |  |  |  |  |  |  | Unit Cost | Total Cost | Total Print time (hr) | Total filament (g)
Version: V1.0 |  | Last Updated: 2024-June-18 |  |  |  |  |  | $20.03 | $20.03 | 1.55 | 68
Commercial Parts
ID | Part Name | Part Type | QTY | QTY/PKG | $/PKG | PKG QTY | $/Unit | Extended | Total | Link
 | Mini 2-Axis Analog Thumbstick | Electrical | 1 | 1 | $3.87 | 1 | $3.87 | $3.87 | $3.87 | https://www.digikey.ca/en/products/detail/adafruit-industries-llc/2765/6193582
 | Analog Mini Thumbstick Breakout Board | Electrical | 1 | 1 | $2.18 | 1 | $2.18 | $2.18 | $2.18 | https://www.digikey.ca/en/products/detail/adafruit-industries-llc/3246/6193594
 | 3.5 mm stereo cable (4 conductor, TRRS, M-M) | Electrical | 1 | 1 | $5.09 | 1 | $5.09 | $5.09 | $5.09 | https://www.digikey.ca/en/products/detail/tensility-international-corp/10-00332/2350238
 | M3 hex nut x2 | Mechanical | 2 | 1 | $0.28 | 2 | $0.28 | $0.56 | $0.56 | https://www.digikey.ca/en/products/detail/keystone-electronics/4708/4499301
 | (Optional for mount) M3x12mm screw x2 | Mechanical | 0 | 1 | $1.11 | 0 | $1.11 | $- | $- | https://www.digikey.ca/en/products/detail/apm-hexseal/RM3X12MM-2701/2063201
 | (Optional for mount) Tee nut | Mechanical | 0 | 1 | $0.48 | 0 | $0.48 | $- | $- | https://www.homedepot.ca/product/paulin-1-4-inch-20-tee-nuts-4-prong-5-16-inch-barrel-length/1000129429
 | Digikey shipping (if spending less than $100) | Shipping | 1 | 1 | $8.00 | 1 | $8.00 | $8.00 | $8.00
3D Printed Parts ESTIMATED PRICING USING 1KG ROLL COST: |  | $25.00
ID | Part | Material | QTY | Mass (g) / Unit | Time / Unit |  | Print Time (Min) | Estimated Unit Price | Total Price | Link
 | Aspen_Enclosure_Bottom | PLA | 1 | 8.0 | 61 |  | 61 | $0.20 | $0.20
 | Aspen_Enclosure_Top | PLA | 1 | 4.6 | 28 |  | 28 | $0.12 | $0.12
 | Inner cover disk | PLA | 1 | 0.5 | 4 |  | 4 | $0.01 | $0.01
 | (Optional) Joystick_Camera_Mount_Adapter | PLA | 0 | 6.5 | 43 |  | 0 | $0.16 | $-
 | (Optional) Joystick_RAM_B_Mount_Adapter | PLA | 0 | 9.3 | 61 |  | 0 | $0.23 | $-
 | (Optional) Aspen_Hand_Support | PLA | 0 | 38.5 | 189 |  | 0 | $0.96 | $-
 | (Optional) Topper - small dome | PLA | 0 | 0.6 | 8 |  | 0 | $0.02 | $-
 | (Optional) Topper - medium dome | PLA | 0 | 1.7 | 17 |  | 0 | $0.04 | $-
 | (Optional) Topper - large dome | PLA | 0 | 4.9 | 37 |  | 0 | $0.12 | $-
 | (Optional) Topper - ring | PLA | 0 | 1.5 | 16 |  | 0 | $0.04 | $-
 | (Optional) Topper - concave | PLA | 0 | 1 | 10 |  | 0 | $0.03 | $-
 |  |  |  |  |  |  |  | $- | $-
Tools for Assembly
 | Flush cutters
 | Wire strippers
 | Soldering iron
 | Philips head screw driver
 | 3D printer
 | (Optional for mount adapter) 1/4-20 screw or hex bolt, at least 1/2" long |  |  |  |  |  |  |  |  | https://www.homedepot.ca/product/paulin-1-4-20-x-1-2-inch-hex-head-cap-screw-18-8-stainless-steel-unc/1000142251
Alternatives (if there are other sources for some parts link them below)
ID | Part and description | Part Type | QTY | QTY/PKG | $/PKG | PKG QTY | $/Unit | Extended | Total | Link
 | Analog Mini Thumbstick Breakout Board - Adafruit | Electrical | 1 | 1 | $1.50 | 1 | $1.50 | $1.50 | $1.50 | https://www.adafruit.com/product/3246
 | Mini 2-Axis Analog Thumbstick | Electrical | 1 | 1 | $2.50 | 1 | $2.50 | $2.50 | $2.50 | https://www.adafruit.com/product/2765
 | 3.5 mm 4C TRRS M-M Cable | Electrical | 0.5 | 1 | $2.89 | 1 | $2.89 | $1.45 | $2.89 | https://www.primecables.ca/p-370661-cab-aud-260-all-35mm-18-inch-4c-trrs-male-to-male-28awg-ft4-cable-black?from_pla=google&sku=383487
 | 3.5 mm 4C TRRS M-M Cable |  | 0.5 | 1 | $6.71 | 1 | $6.71 | $3.36 | $6.71 | https://www.digikey.ca/en/products/detail/tensility-international-corp/10-02155/7606602
 | (Optional for mount) M3x10mm screws and nuts x2 | Mechanical | 4 | 340 | $22.14 | 1 | $0.07 | $0.26 | $22.14 | https://a.co/d/0B9sK8N
 | TRRS Audio Cable | DigiKey | 1 | 1 | $7.19 | 1 | $7.19 | $7.19 | $7.19 | https://www.digikey.ca/en/products/detail/tensility-international-corp/10-00341/2350244

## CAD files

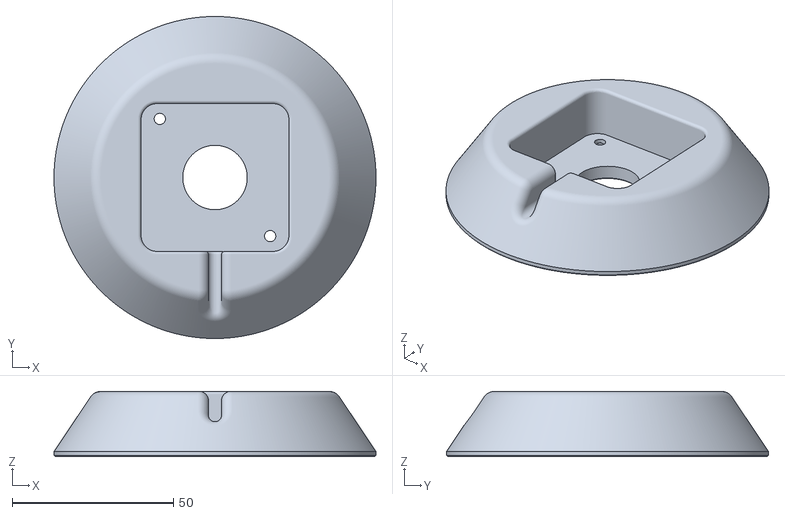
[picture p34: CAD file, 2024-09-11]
Build_Files/3D_Print_Files/Aspen_Hand_Support.stl
100.0 x 100.0 x 20.3

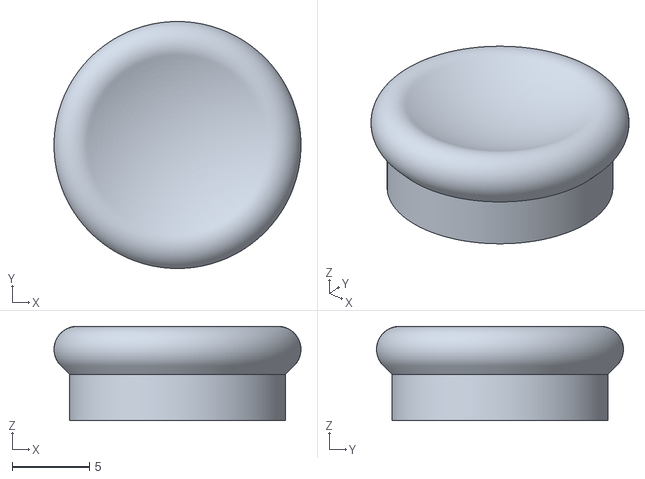
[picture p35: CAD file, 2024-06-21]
Build_Files/3D_Print_Files/Toppers/Sliding_Topper_Concave.stl
16.0 x 16.0 x 6.12

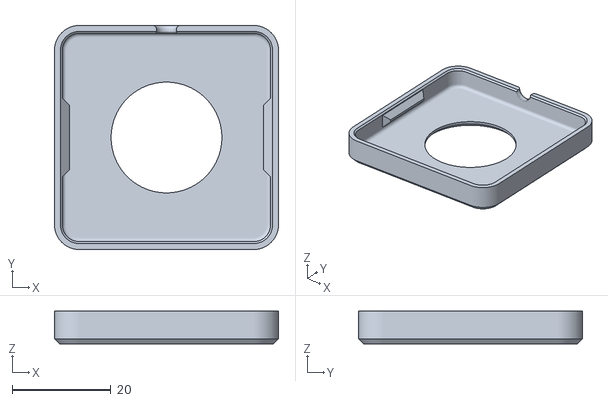
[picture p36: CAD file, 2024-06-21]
Build_Files/3D_Print_Files/Aspen_Enclosure_Top.stl
45.3 x 45.3 x 6.60

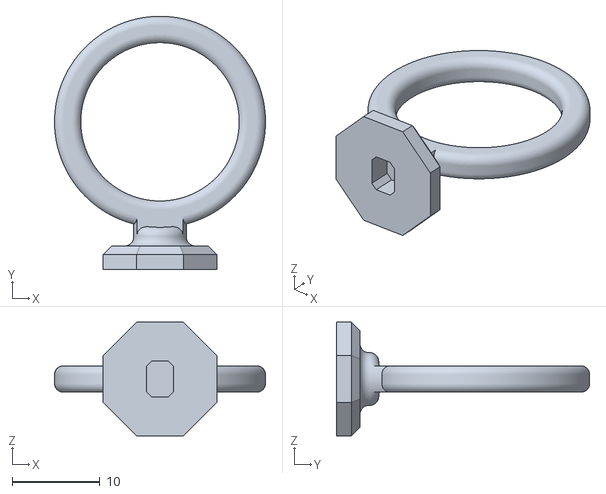
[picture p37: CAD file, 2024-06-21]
Build_Files/3D_Print_Files/Toppers/Sliding_Topper_Ring.stl
24.0 x 28.8 x 12.9

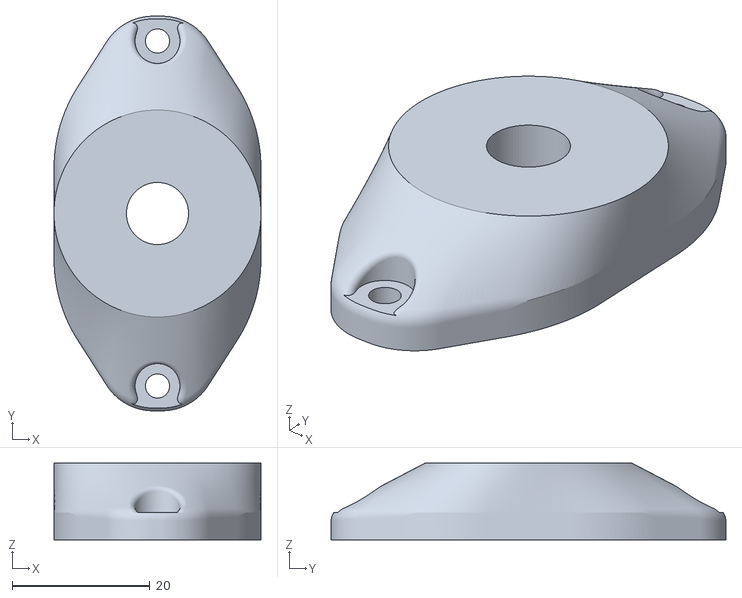
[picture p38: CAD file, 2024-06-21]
Build_Files/3D_Print_Files/Joystick_Camera_Mount_Adapter.stl
30.0 x 57.2 x 11.1

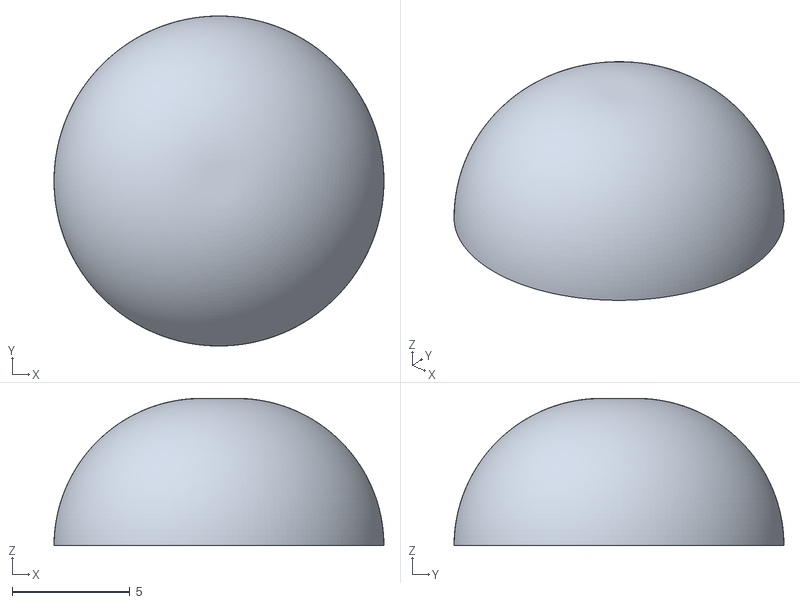
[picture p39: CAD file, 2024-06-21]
Build_Files/3D_Print_Files/Toppers/Sliding_Topper_Small_dome.stl
14.0 x 14.0 x 6.25

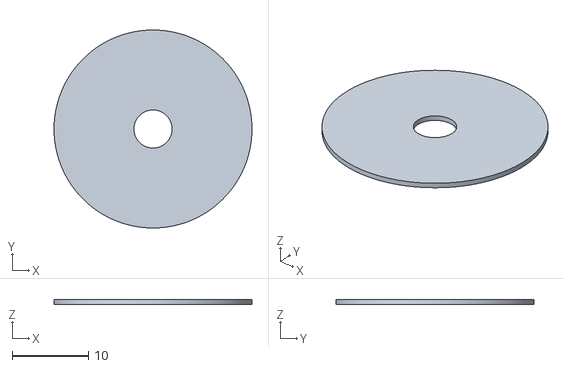
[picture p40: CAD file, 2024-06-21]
Build_Files/3D_Print_Files/Aspen_Inner_cover_disk.stl
26.0 x 26.0 x 0.6

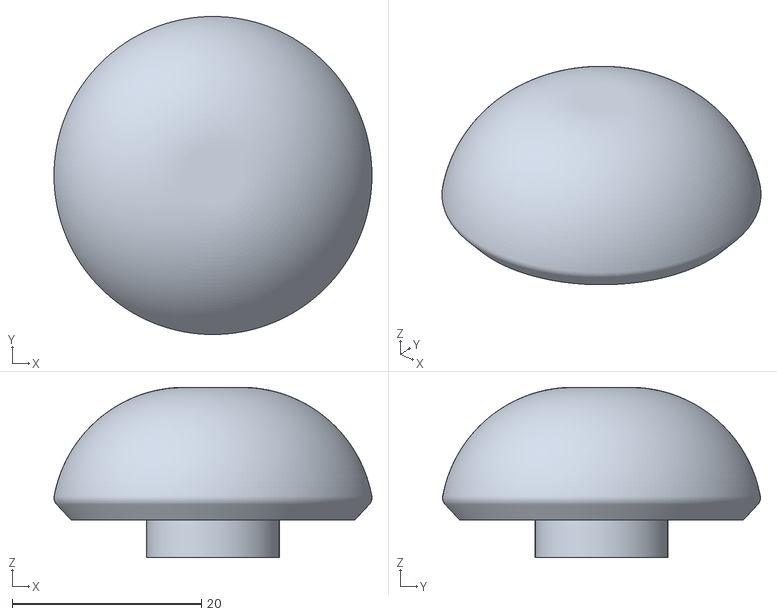
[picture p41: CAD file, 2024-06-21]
Build_Files/3D_Print_Files/Toppers/Sliding_Topper_Large_dome.stl
33.6 x 33.6 x 18.0

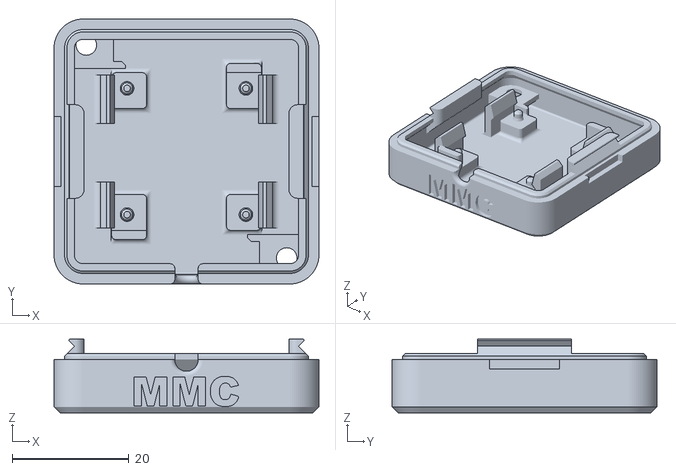
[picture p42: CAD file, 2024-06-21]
Build_Files/3D_Print_Files/Aspen_Enclosure_Bottom.stl
45.3 x 45.3 x 12.6

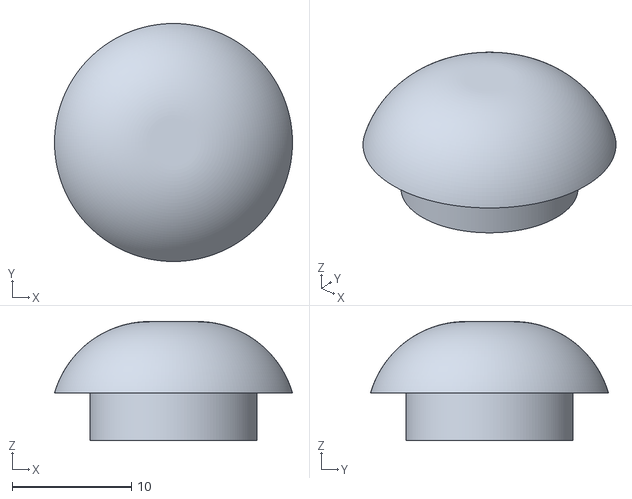
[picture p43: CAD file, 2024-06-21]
Build_Files/3D_Print_Files/Toppers/Sliding_Topper_Medium_dome.stl
20.0 x 20.0 x 10.0

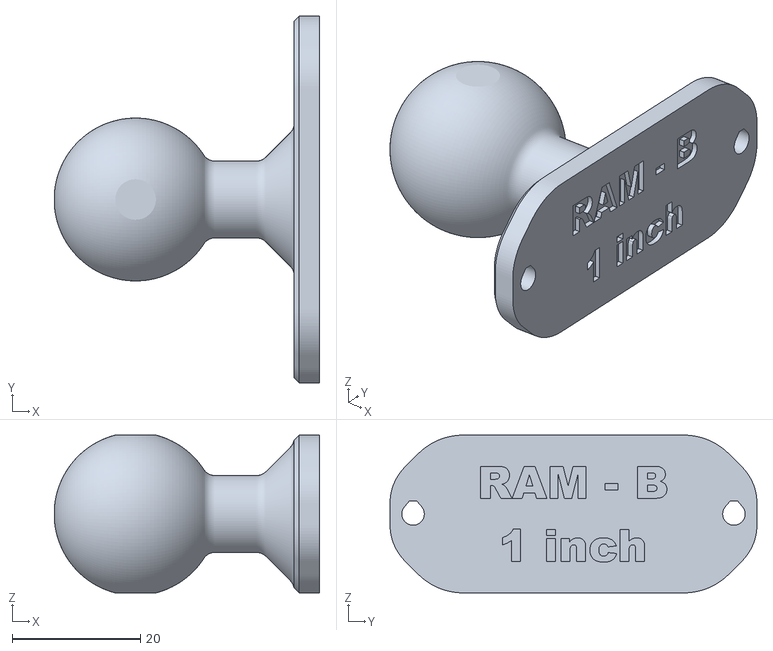
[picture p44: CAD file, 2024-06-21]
Build_Files/3D_Print_Files/Joystick_RAM_B_Mount_Adapter.stl
41.4 x 57.2 x 24.6

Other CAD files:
Design_Files/Aspen Hand Support Medium v6.f3z
Design_Files/Aspen Sliding Joystick v1.0 v20.f3z
Design_Files/Inner cover disk v6.f3d
Design_Files/Joystick RAM Mount Adapter v5.f3d
Design_Files/Joystick_Camera_Mount Narrow v3.f3d
Design_Files/Topper - concave v2.f3d
Design_Files/Topper - large dome v3.f3d
Design_Files/Topper - medium dome v4.f3d
Design_Files/Topper - ring v5.f3d
Design_Files/Topper - small dome v8.f3d

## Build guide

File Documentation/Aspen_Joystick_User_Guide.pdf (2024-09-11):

V1.1 | SEPTEMBER 2024

## Aspen Sliding Joystick

## USER QUICK GUIDE

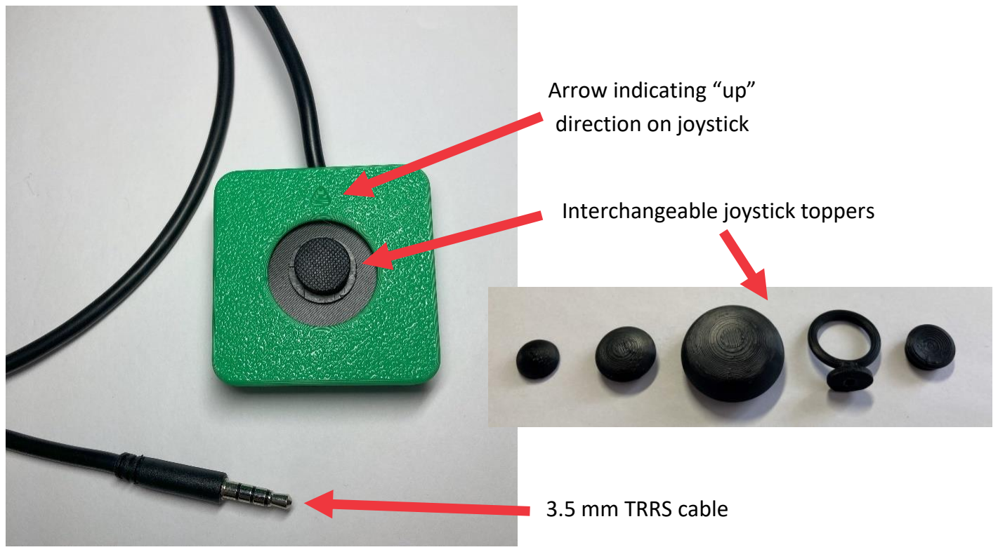
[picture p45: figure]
Arrow indicating “up” direction on joystick; Interchangeable joystick toppers; 3.5 mm TRRS cable
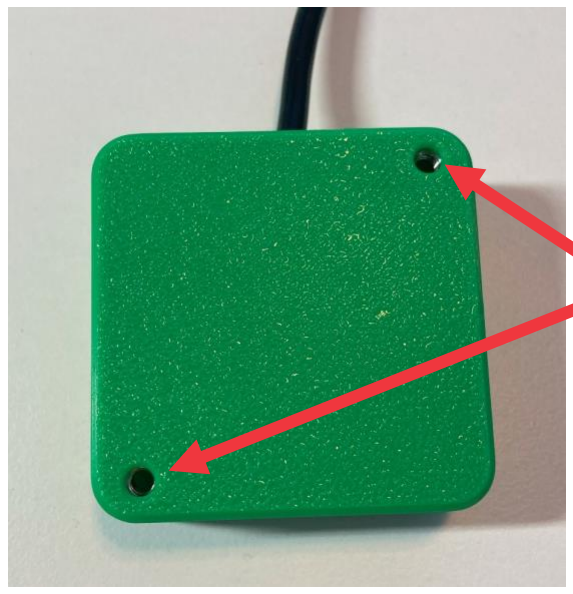
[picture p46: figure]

© 2024 by Neil Squire. (https://neilsquire.ca/)
This work is licensed under the CC BY SA 4.0 License: http://creativecommons.org/licenses/by-sa/4.0
Files available at https://github.com/makersmakingchange/Aspen-Sliding-Joystick | Page 1 of 6

### Introduction

The Aspen Sliding Joystick is a small analog gaming joystick that moves in a sliding motion instead of the typical pivoting motion of a joystick or thumbstick. It has a relatively small range of motion and a moderately low force required. It has a 3.5 mm TRRS plug (the size of a headphone jack) and can be used with the Forest Joystick Mouse Hub, the Xbox Adaptive Controller (XAC) or PlayStation Access Controller.

### Features

Mounting holes

Screw holes for mount
adapters

## USER QUICK GUIDE

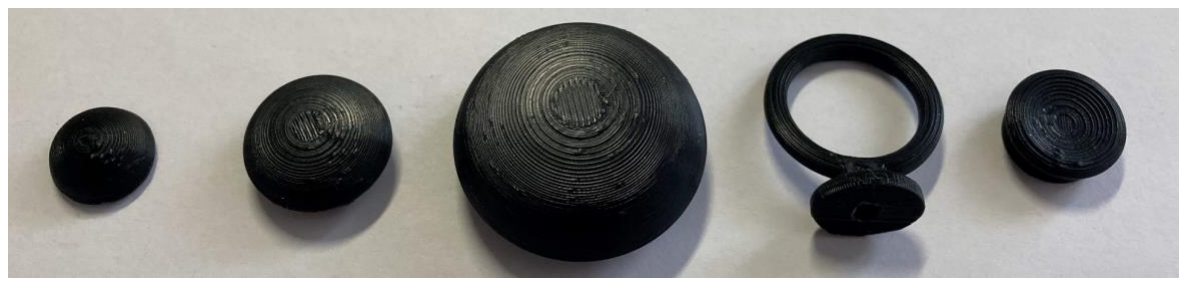
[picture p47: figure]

Files available at https://github.com/makersmakingchange/Aspen-Sliding-Joystick | Page 2 of 6

### Usage

Compatibility
The Aspen Sliding Joystick is compatible with the Forest Joystick Mouse Hub, Xbox Adaptive Controller (XAC) and PlayStation Access Controller. It may be compatible with other interfaces that use joysticks with 3.5 mm TRRS cables, such as the Enabled Controller. (https://makersmakingchange.com/project/enabled-controller/)

Using the Joystick
1. Plug the 3.5 mm TRRS cable from the joystick into the compatible host device. If using the Xbox Adaptive Controller, plug it into X1 to use at the left joystick, or plug into X2 to use as the right joystick.
2. Ensure the arrow on the joystick is pointing in the “up/forward” direction, away from the user.
3. Mount the device if needed (see below).
4. Move joystick as you would with a standard controller.

Changing the Joystick Topper
There are a variety of toppers that can be 3D printed for this joystick, shown below. These toppers will work on either the Aspen Sliding Joystick or the Birch Sliding Joystick

To use them:

1. Remove the original joystick topper by pulling it off, revealing a small peg underneath
2. Take the 3D printed topper, check that it is in the correct orientation and press it onto the joystick. The fit should be snug.

## USER QUICK GUIDE

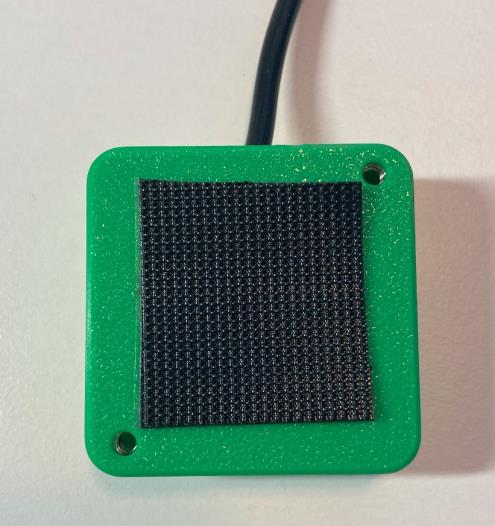
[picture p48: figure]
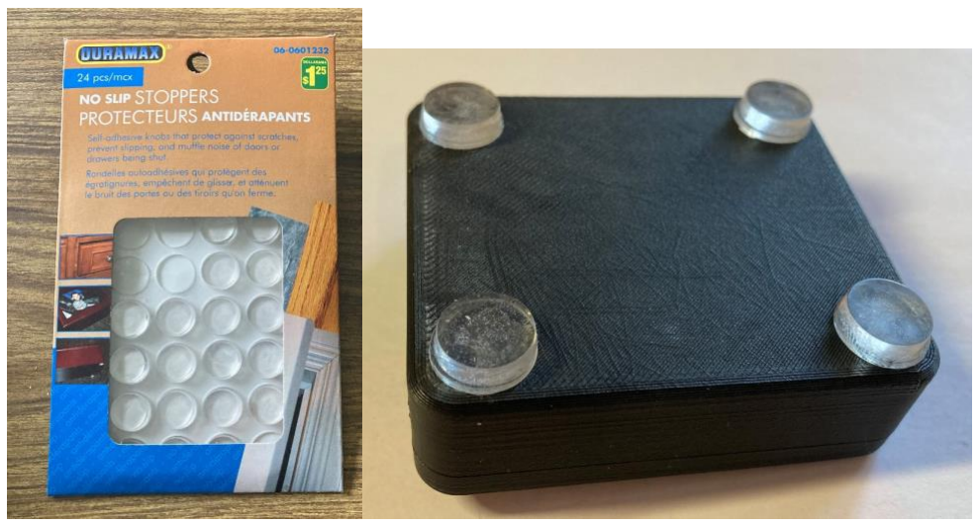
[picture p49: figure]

Files available at https://github.com/makersmakingchange/Aspen-Sliding-Joystick | Page 3 of 6

Mounting the Joystick
The Aspen Sliding Joystick can be mounted in a variety of ways, primarily either on a tabletop or other surface, or by using a mount adapter with a mounting system. For tabletop or lap tray use, the joystick can be secured using hook and loop fasteners, or a non slip material such as non slip stoppers. For use with a mounting system there are mount adapters for either a ¼-20 threaded camera mount or a RAM mount system.

Tabletop – Hook and Loop Fastener
One way the joystick can be mounted, is on a tabletop or other surface such as a lap tray, and fastened using a hook and loop fastener such as Velcro.

Typically, best practice is to stick the side with the loops (the softer side) to the tabletop or other surface, and to stick the side with the hooks (rough side) to the joystick.

Tabletop – Non slip pads
Another way the joystick can be use on the tabletop is by using a non slip material, such as the non slip stoppers shown below, or a non slip material such as Dycem.

## USER QUICK GUIDE

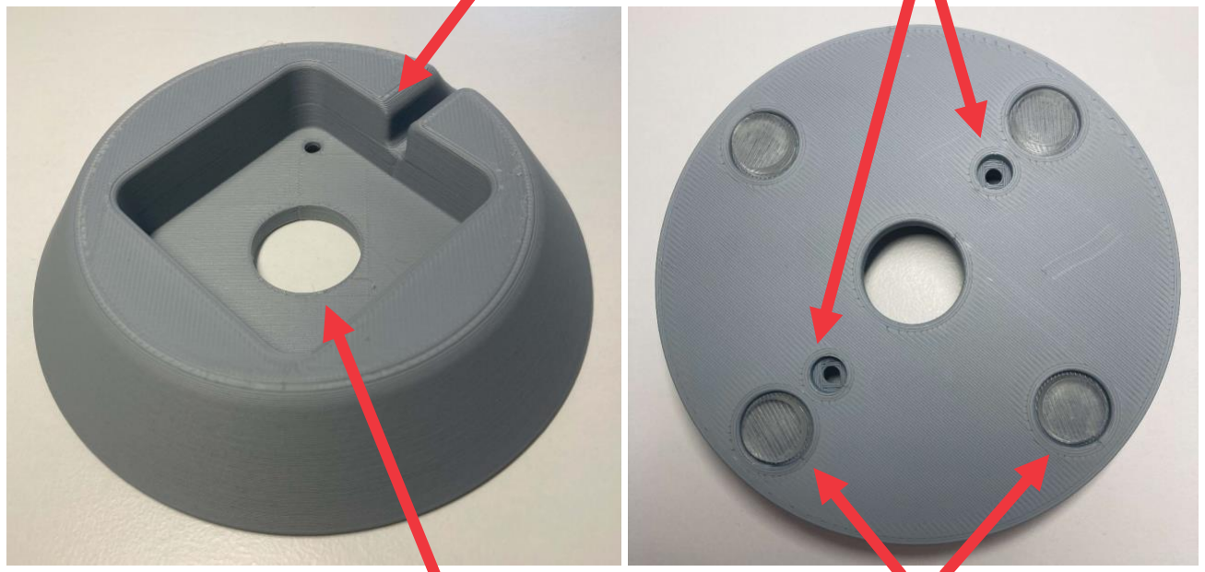
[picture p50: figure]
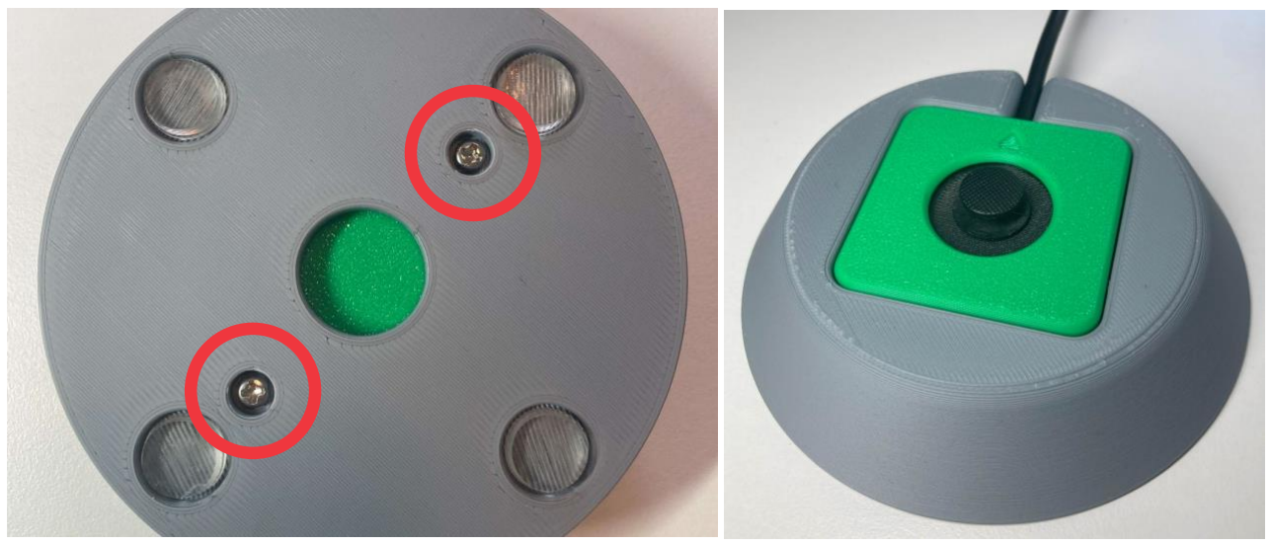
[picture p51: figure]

Files available at https://github.com/makersmakingchange/Aspen-Sliding-Joystick | Page 4 of 6

Tabletop – Aspen Hand Support
The Aspen Hand Support can be used for tabletop use where the user would like a larger surface to rest their hand on.

Aspen Hand Support:

To use, slide the Aspen Joystick into the hand support with the cable going through the cable slot. If the joystick is going to stay in the hand support and you want a more secure connection, you can screw it to the hand support using two M3 nuts in the bottom of the hand support as pictured:

Screw holes to attach
to joystick

Non slip pads (x4)

Cable slot

Hole for easy removal

## USER QUICK GUIDE

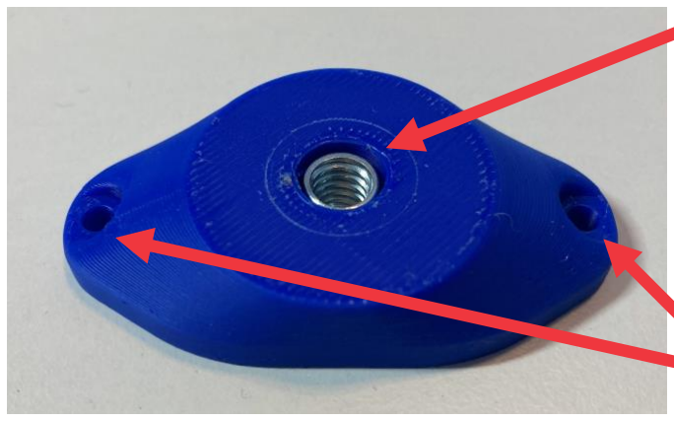
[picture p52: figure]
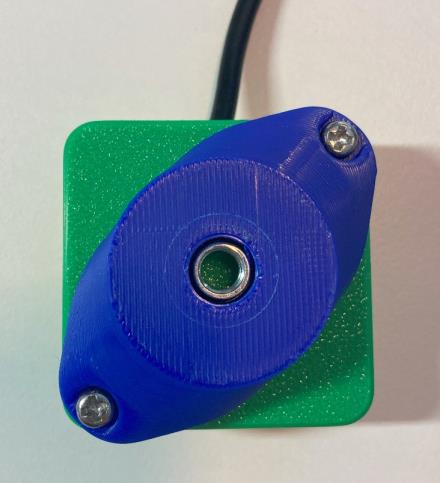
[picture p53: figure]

Files available at https://github.com/makersmakingchange/Aspen-Sliding-Joystick | Page 5 of 6

¼-20 Threaded Camera Mount
Another way the joystick can be mounted is by using a mount with a ¼-20 thread on the end, such as a commercially available camera mount. To mount the joystick on a ¼-20 thread, the Camera Mount Adapter is used. The assembly for this Camera Mount Adapter is found in the Maker Guide.

Camera Mount Adapter:

This is then screwed onto the bottom of the joystick, as shown here, using two M3 screws that are at least 10 mm long. Now, the joystick can be mounted on a mount with ¼-20 thread, such as a typical camera mount.

Screw holes to attach
to joystick

¼-20 thread for camera mount

## USER QUICK GUIDE

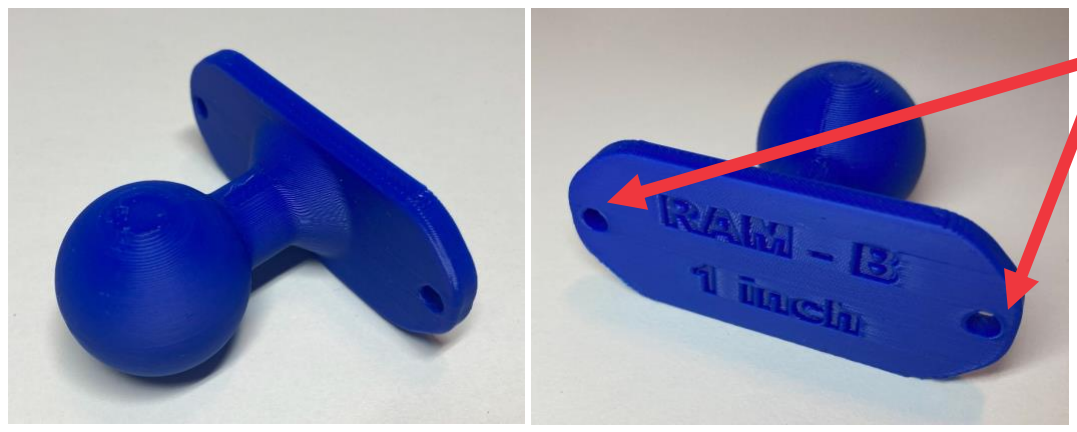
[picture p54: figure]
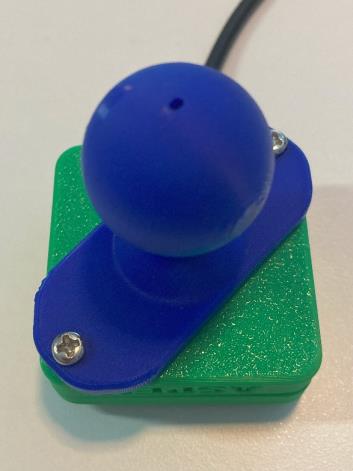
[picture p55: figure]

Files available at https://github.com/makersmakingchange/Aspen-Sliding-Joystick | Page 6 of 6

RAM B Mount
Another way the joystick can be mounted is by using a commercially available RAM B compatible mount with a 1” ball and socket system. For this, the Joystick RAM Mount Adapter is used.

This is then screwed onto the bottom of the joystick, as shown here, using two M3 screws that are at least 10 mm long. Now, the joystick can be mounted RAM B Compatible Mounting System.

### Specifications

Total height (with default topper) | 1.9 cm
Enclosure height | 1.6 cm
Enclosure width | 4.5 cm
Enclosure length | 4.5 cm
Weight (including TRRS cable) | 40 grams
Range of motion | ±2 mm
Activation force (to full deflection) | 115 grams of force

### Cleaning

The Aspen Sliding Joystick can be wiped down with a damp cloth. Do not use hot water on this device or the plastic housing may warp. Do not submerge the device.

Screw holes to attach
to joystick

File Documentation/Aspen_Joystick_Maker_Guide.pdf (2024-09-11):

V1.1 | SEPTEMBER 2024

## Aspen Sliding Joystick

## MAKER GUIDE

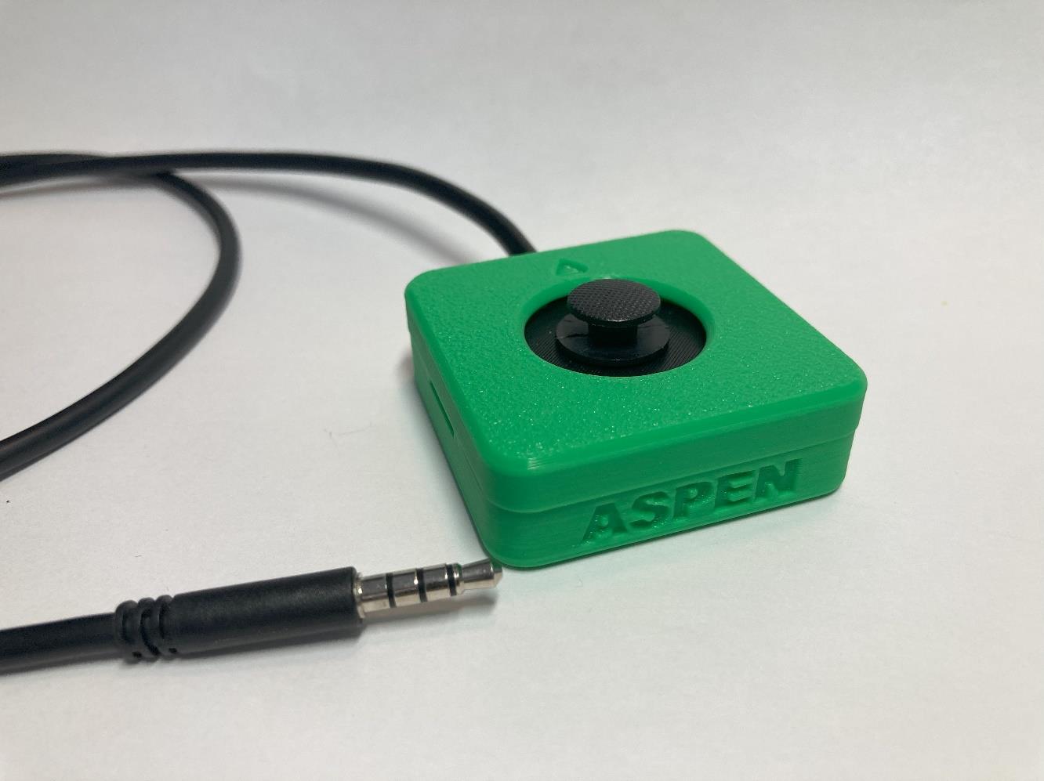
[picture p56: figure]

© 2024 by Neil Squire Society. (https://www.neilsquire.ca/) This work is licensed under the CC BY SA 4.0 License: http://creativecommons.org/licenses/by-sa/4.0
Files available at https://github.com/makersmakingchange/Aspen-Sliding-Joystick | Page 1 of 25

### Overview

This document contains the necessary information to build the Aspen Sliding Joystick, including a customization guide, 3D printing guide, assembly guide, and instructions to test the finished joystick.

## MAKER GUIDE

Files available at https://github.com/makersmakingchange/Aspen-Sliding-Joystick | Page 2 of 25

### Contents

Overview | 1
Maker To Do List | 4
Items to Give to User | 4
Customization Guide | 5
Joystick | 5
Toppers | 5
Mounting | 5
3D Printing Guide | 6
3D Printing Summary | 6
3D Printing Settings | 6
Joystick Enclosure - REQUIRED | 6
Toppers and Mount Adapters* - OPTIONAL | 6
Post-Processing | 7
Examples of Quality Prints | 7
Assembly Guide | 10
Required Components | 10
Required Tools | 10
Optional Tools | 10
Required Personal Protective Equipment (PPE) | 10
Joystick Assembly | 11
Step 1: Solder Joystick to Breakout Board | 11
Step 2: Prepare Audio Cable | 11
Step 3: Identify Audio Cable Wires | 12
Step 4: Wire the Joystick | 12
Step 6: Check for Shorts | 14
Step 7: Insert M3 Hex Nuts | 15
Step 8: Insert Joystick Into Enclosure | 15
Step 9: Route TRRS Cable | 16
Step 10: Position Joystick Inner Disk | 16

## MAKER GUIDE

Files available at https://github.com/makersmakingchange/Aspen-Sliding-Joystick | Page 3 of 25
Step 11: Assemble Enclosure | 17
Step 13: Joystick Assembly Complete | 17
Testing | 18
Testing using a Multimeter | 18
Testing using an USB-HID Gamepad Interface Device | 20
Optional – Mounting | 21
Table Top Mounting – Non-Slip Pads | 21
Table Top Mounting – Hook and Loop Fastener | 21
Camera Mount | 22

## MAKER GUIDE

Files available at https://github.com/makersmakingchange/Aspen-Sliding-Joystick | Page 4 of 25

This list provides an overview of the steps required to build and deliver the device.

### Maker To Do List

Read through the Maker Guide to become familiar with required components, tools, supplies, safety gear, and overall assembly steps.
Ask the user if they would if they have a device to connect the joystick to.
- Xbox Adaptive Controller (https://www.xbox.com/en-CA/accessories/controllers/xbox-adaptive-controller)
- PlayStation Access Controller (https://www.playstation.com/en-ca/accessories/access-controller/)
- Forest Joystick Mouse Hub (https://github.com/makersmakingchange/Forest-Joystick-Mouse-Hub)
- Enabled Controller Mini (https://github.com/makersmakingchange/Enabled-Controller-Mini/tree/main)
- Enabled Controller (https://github.com/milador/Enabled-Controller)
- Other Analog to USB joystick hub
Ask the user if they would like any joystick toppers.
Ask the user if they would like a specific mounting solution.
- Tabletop
- Hook and Loop Fasteners
- Non slip material
- Camera Mount Adapter
- RAM Mount Adapter
Talk to User about customization options (e.g., colour, any special requests, etc.). Order hardware components.
3D print all 3D printed components.
Gather tools, supplies, and safety equipment.
Assemble the device.
Test device.
Print “User Guide”

### Items to Give to User

Assembled, tested device
Any joystick toppers if requested. Any mount adapters if requested. “User Guide”

## MAKER GUIDE

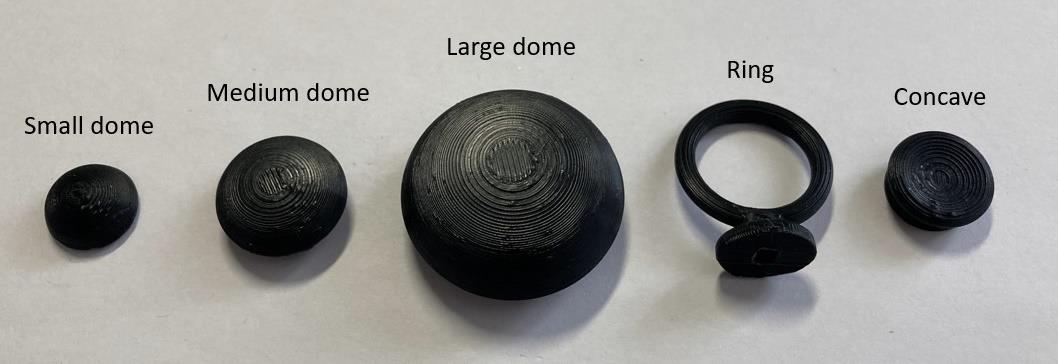
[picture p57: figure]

Files available at https://github.com/makersmakingchange/Aspen-Sliding-Joystick | Page 5 of 25

### Customization Guide

### Joystick

The enclosure can be printed in the user’s desired colour(s). Colour swaps can be done to further customize the joystick and make the forward arrow on the top stand out more.

### Toppers

3D printed joystick toppers can be added to the joystick. Current topper type include the small dome, medium dome, large dome, ring, and concave (shown left to right). These toppers can also be modified through the original design files.

### Mounting

Mount adapters can be added for custom mounting solutions. Current mounting options include nonslip pads, hook and loop fastener, and a ¼-20 camera mount adapter.

## MAKER GUIDE

Files available at https://github.com/makersmakingchange/Aspen-Sliding-Joystick | Page 6 of 25

### 3D Printing Guide

### 3D Printing Summary

Metrics | Joystick Enclosure | All Toppers
Total Print Time (min) | 1h34m | 1h28m
Total Number of Components | 3 | 5
Typical Total Mass (g) | 13.2 | 9.7
Typical Number of Print Setups | 1 | 1

### 3D Printing Settings

Joystick Enclosure - REQUIRED
Print File Name | Qty | Total Print Time (hr:min)* | Mass (g) | Infill (%) | Support (Y/N) | Layer Height/ Nozzle Diameter(mm) | Notes
Aspen_Enclosure_ Bottom | 1 | 1:02 | 8.1 | 20 | N | 0.2/0.4
Aspen_Enclosure_Top | 1 | 0:28 | 4.6 | 20 | N | 0.2/0.4
Aspen_Inner_cover_disk | 1 | 0:04 | 0.5 | 20 | N | 0.2/0.4

Toppers and Mount Adapters* - OPTIONAL
Print File Name | Qty | Total Print Time (hr:min)* | Mass (g) | Infill (%) | Support (Y/N) | Layer Height/ Nozzle Diameter(mm) | Notes
Joystick_Camera_ Mount_Adapter | 1 | 0:43 | 6.5 | 20 | Y | 0.2/0.4
Joystick_RAM_B_Mount_ Adapter | 1 | 1:01 | 9.3 | 20 | Y | 0.2/0.4
Aspen_Hand_Support | 1 | 3:09 | 38.5 | 20 | N | 0.2/0.4
Sliding_Topper_Small_ dome | 1 | 0:08 | 0.6 | 20 | N | 0.2/0.4
Sliding_Topper_Medium_ dome | 1 | 0:17 | 1.7 | 20 | Y | 0.2/0.4
Sliding_Topper_Large_ dome | 1 | 0:37 | 4.9 | 20 | Y | 0.2/0.4
Sliding_Topper_Ring | 1 | 0:16 | 1.5 | 20 | Y | 0.2/0.4 | Print with ring parallel to print bed
Sliding_Topper_Concave | 1 | 0:10 | 1.0 | 20 | N | 0.2/0.4
*Print times are based off of an Ender 3 S1 printer

## MAKER GUIDE

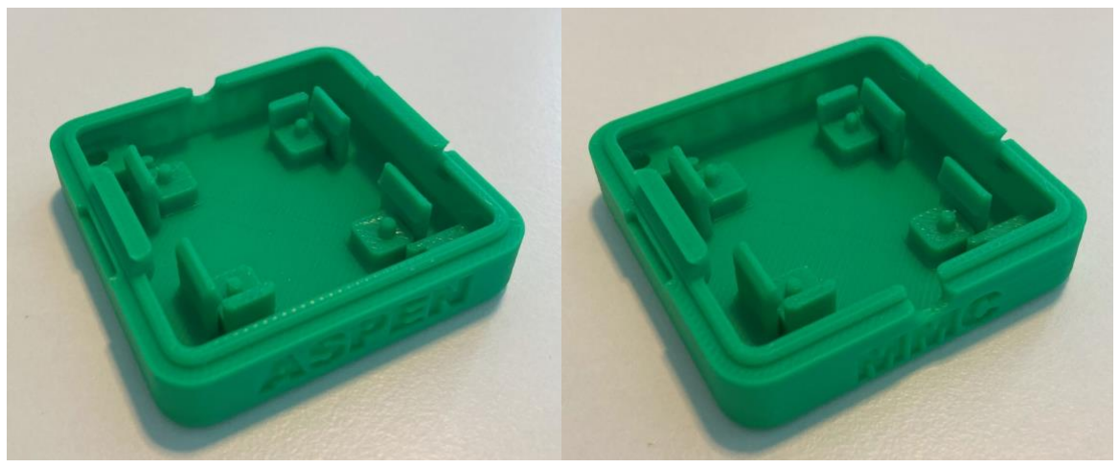
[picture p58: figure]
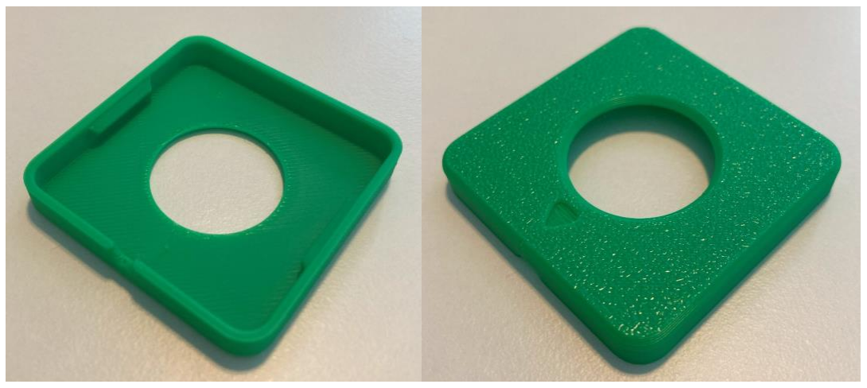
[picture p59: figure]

Files available at https://github.com/makersmakingchange/Aspen-Sliding-Joystick | Page 7 of 25

### Post-Processing

- Remove any bumps or zits from the surface where the enclosure meets the lid.
- Remove any bumps or zits from both surfaces of the inner cover disk. If any binding occurs between the joystick and the inner cover disk when assembling, sand down this part.
- Remove any supports from camera mount or toppers if printed.

### Examples of Quality Prints

Photos of Enclosure 3D Prints

Enclosure Bottom

Enclosure Top

## MAKER GUIDE

Files available at https://github.com/makersmakingchange/Aspen-Sliding-Joystick | Page 8 of 25

Inner Cover Disk

Photos of Joystick Camera Mount Adapter 3D Print

Photos of RAM Mount Adapter 3D Print

## MAKER GUIDE

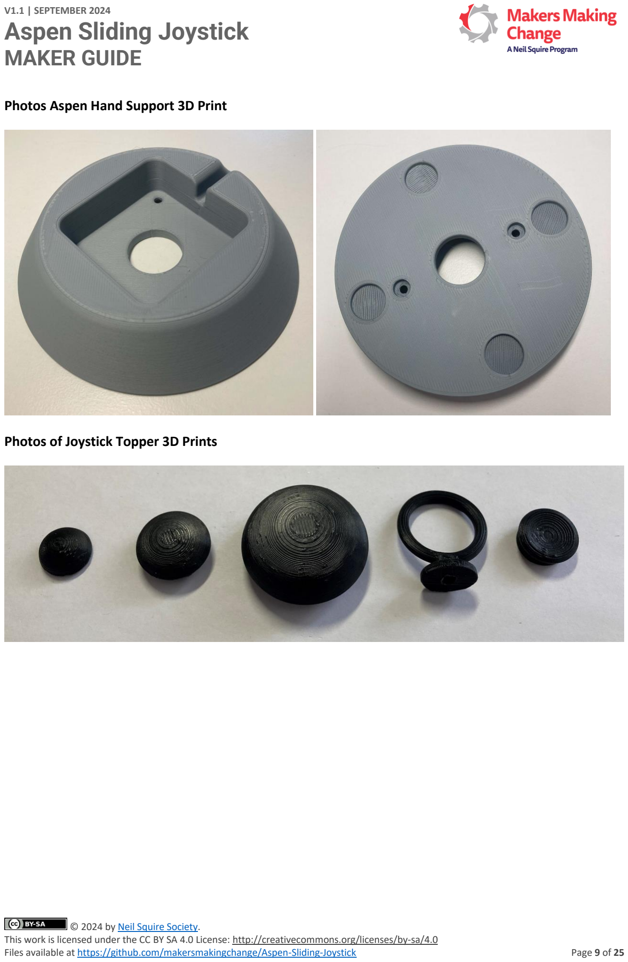
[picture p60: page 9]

Files available at https://github.com/makersmakingchange/Aspen-Sliding-Joystick | Page 9 of 25

Photos Aspen Hand Support 3D Print

Photos of Joystick Topper 3D Prints

## MAKER GUIDE

Files available at https://github.com/makersmakingchange/Aspen-Sliding-Joystick | Page 10 of 25

### Assembly Guide

### Required Components

1

Mini 2-Axis
Analog
Thumbstick

QTY 1 2

Analog Mini
Thumbstick
Breakout Board

QTY 1 3

TRRS Audio
Cable | QTY 1
4 | M3 Hex Nuts | QTY 2 | 5 | Aspen Inner Disk | QTY 1 | 6

Aspen Enclosure
Bottom | QTY 1

7

Aspen
Enclosure Top QTY 1

### Required Tools

- Flush Cutters
- Wire Strippers
- Soldering Iron and Solder
- Multimeter (with continuity testing capabilities)

### Optional Tools

- Tweezers

### Required Personal Protective Equipment (PPE)

- Safety Goggles

## MAKER GUIDE

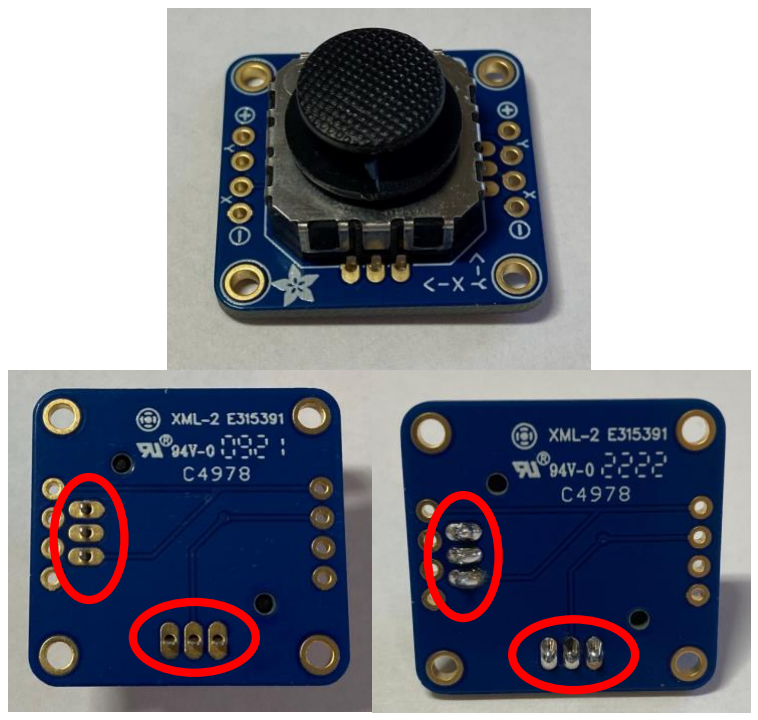
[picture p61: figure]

Files available at https://github.com/makersmakingchange/Aspen-Sliding-Joystick | Page 11 of 25

### Joystick Assembly

Step 1: Solder Joystick to Breakout Board Insert the mini 2-axis analog thumbstick into the breakout board.

Solder the 6 pins, shown circled in red.

Step 2: Prepare Audio Cable
If you are using the pre-prepared TRRS cable from DigiKey, pictured in the component list, you can skip this step.

If using a different cable, prepare the wires for soldering:
- Cut the TRRS cable to length (typically 1 m).
- Strip off approximately 2 cm of the outer insulation.
- Then, separate the 4 individual inner wires. If there are three insulated wires plus copper strands, twist these copper strands together to be one of your wires. If there are 4 insulated wires plus loose copper stranded wires, cut off these copper wires.
- Strip off approximately 0.5 cm of insulation from the inner wires.
- For each inner wire, twist the inner strands together

## MAKER GUIDE


Files available at https://github.com/makersmakingchange/Aspen-Sliding-Joystick | Page 12 of 25
Step 3: Identify Audio Cable Wires
If using the pre-prepared DigiKey cable, you can skip this step.

If using a different cable, you need to identify which wires correspond to which parts of the plug. Use a multimeter or other continuity tester to confirm. Follow this guide for checking continuity (https://www.youtube.com/watch?v=T4p8UQZqh5U) to determine which wire corresponds to the Sleeve, Ring 1, Ring 2, and Tip of the TRRS cable plug. You can use the table below to write the corresponding colours for your cable.

TRRS Plug | DigiKey TRRS cable | Your TRRS cable
Sleeve | Black
Ring 2 | Green
Ring 1 | White
Tip | Red
Step 4: Wire the Joystick
Wiring the joystick will follow the diagram below and will be broken down into multiple steps.

Figure 1. Joystick Wiring Guide. Image Remixed from Sparkfun, released under a CC BY 2.0 license.

Table 1: Aspen Wiring

Joystick Breakout Board | CONNECTION | Digikey TRRS Cable | Your TRRS Cable
+ | Sleeve (S) | Black
Y | Tip (T) | Red
X | Ring 1 (R1) | White
- | Ring 2 (R2) | Green

## MAKER GUIDE

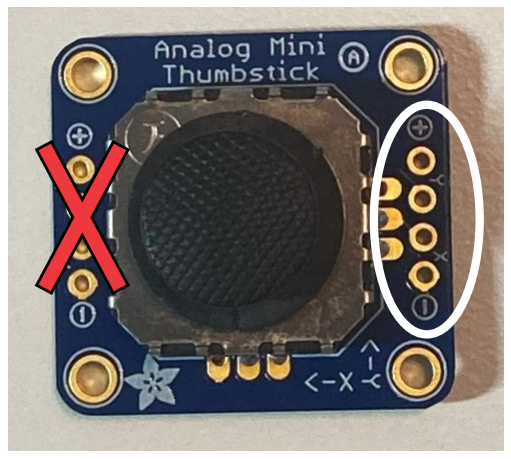
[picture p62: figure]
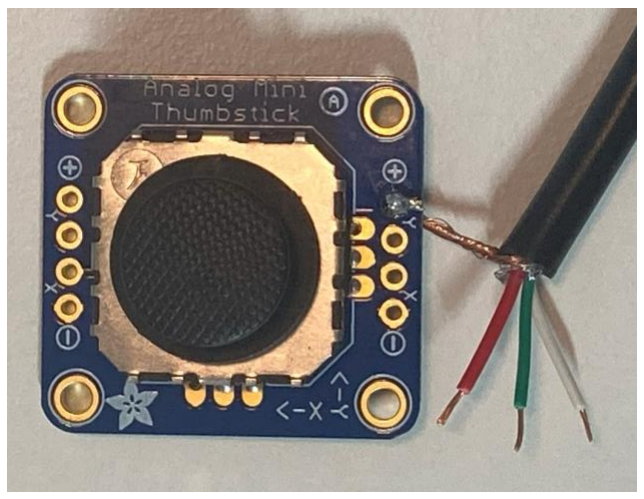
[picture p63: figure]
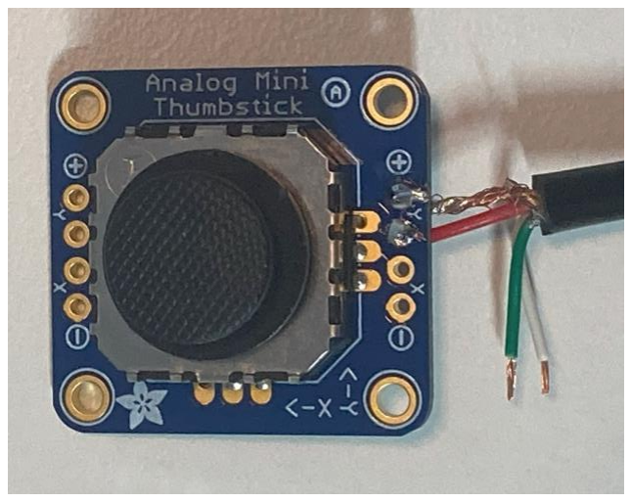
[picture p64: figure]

Files available at https://github.com/makersmakingchange/Aspen-Sliding-Joystick | Page 13 of 25
Step 4A: Identify the Correct Solder Pads

With the joystick breakout board aligned such that the words are at the top and facing you, the pins to solder to are on the right, closest to the text with the “X” and “Y” next to small arrows.

Do not solder to the pins on the left.

Step 4B: Solder TRRS Sleeve to + Pad

Insert the TRRS audio cable sleeve wire (black or copper) into the + Pad on right side of the joystick breakout board, with the wire going in from the bottom of the board to the top.

Solder the wire to the pad on the top of the board.

Step 4C: Solder TRRS Tip to Y Pad

Insert the TRRS audio cable tip wire (red) into the Y Pad on right side of on the joystick breakout board, with the wire going in from the bottom of the board to the top.

Solder the wire to the pad on the top of the board.

## MAKER GUIDE

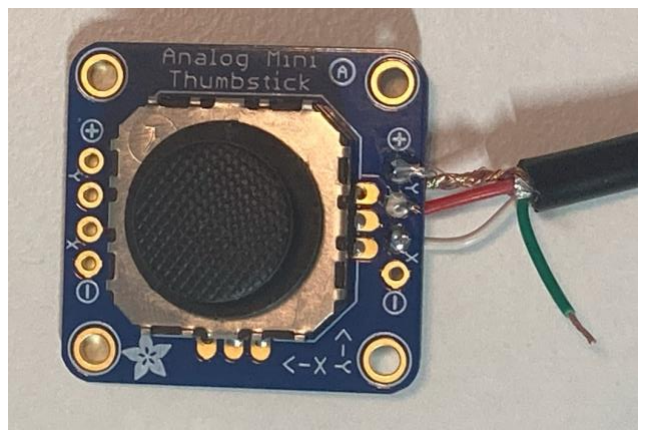
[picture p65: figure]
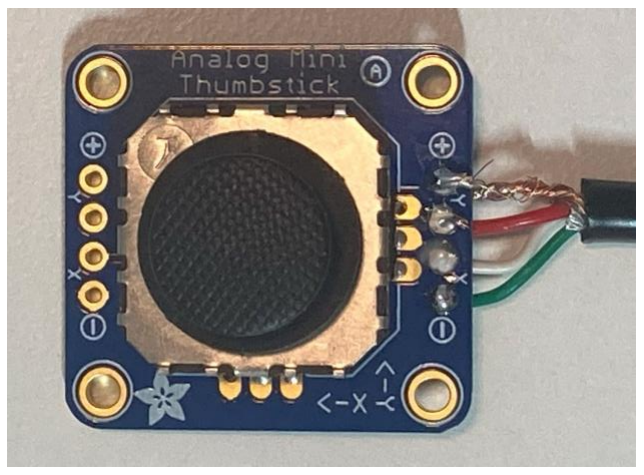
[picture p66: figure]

Files available at https://github.com/makersmakingchange/Aspen-Sliding-Joystick | Page 14 of 25
Step 4D: Solder TRRS R1 to X Pad

Insert the TRRS audio cable Ring 1 wire (white) into the X Pad on right side of on the joystick breakout board, with the wire going in from the bottom of the board to the top.

Solder the wire to the pad on the top of the board.

Step 4E: Solder TRRS R2 to - Pad

Insert the TRRS audio cable Ring 2 wire (green) into the - Pad on right side of on the joystick breakout board, with the wire going in from the bottom of the board to the top.

Solder the wire to the pad on the top of the board.

Step 6: Check for Shorts
Inspect the board and check that none of the connections are shorted.

There should be no bridges/connections between adjacent pins.

If you have a multimeter, you can use it to double check continuity.

If the solder is connecting anything it should not, use the soldering iron and some extra wire, solder wick, or a desoldering tool to remove solder from that area.

## MAKER GUIDE

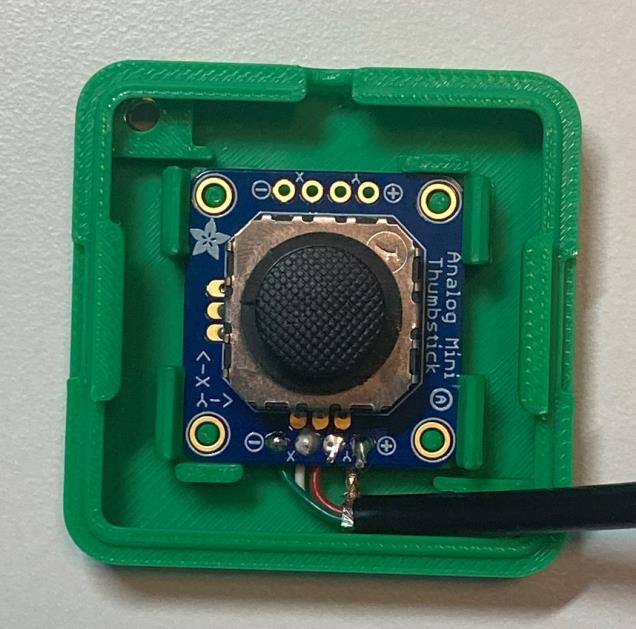
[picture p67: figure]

Files available at https://github.com/makersmakingchange/Aspen-Sliding-Joystick | Page 15 of 25
Step 7: Insert M3 Hex Nuts
Take the enclosure bottom and insert the M3 nuts into the slots as shown. You may require a tool such as needle-nosed pliers or a screwdriver to push the nuts into place.
Step 8: Insert Joystick Into Enclosure

With the enclosure aligned such that the cable goes out away from you, and with the joystick aligned such that the text “Analog Mini Joystick” is to the right, press down on the joystick to snap it into place onto the small mounting posts.

## MAKER GUIDE

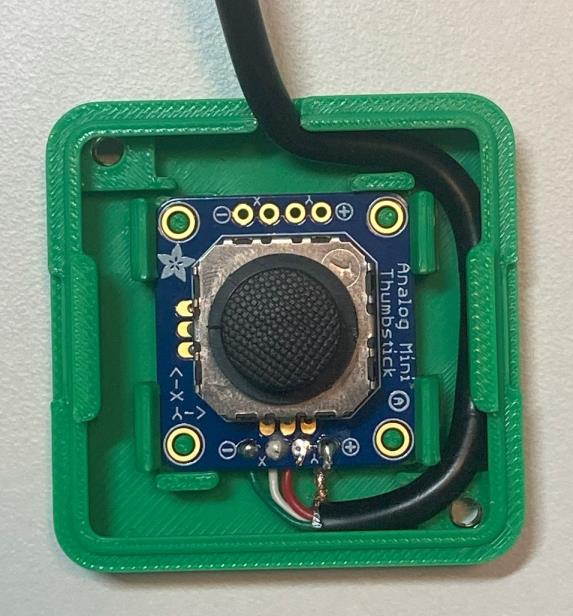
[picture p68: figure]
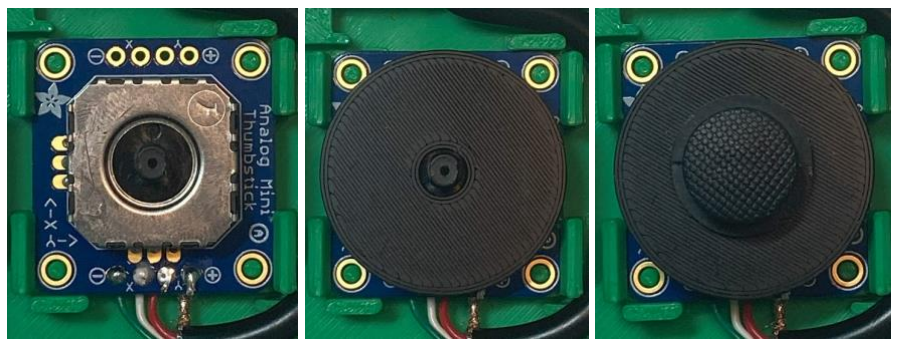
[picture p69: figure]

Files available at https://github.com/makersmakingchange/Aspen-Sliding-Joystick | Page 16 of 25
Step 9: Route TRRS Cable

As shown in the photo, route the cable to the side of the enclosure, between the joystick snap fits and the edge of the enclosure, and then out the hole at the back of the enclosure. You may need to push the cable down to get it past the enclosure snap fit.

Step 10: Position Joystick Inner Disk

Remove the joystick
topper.

Place the 3D printed inner disk on the joystick, around the joystick post.

Replace joystick topper.

## MAKER GUIDE

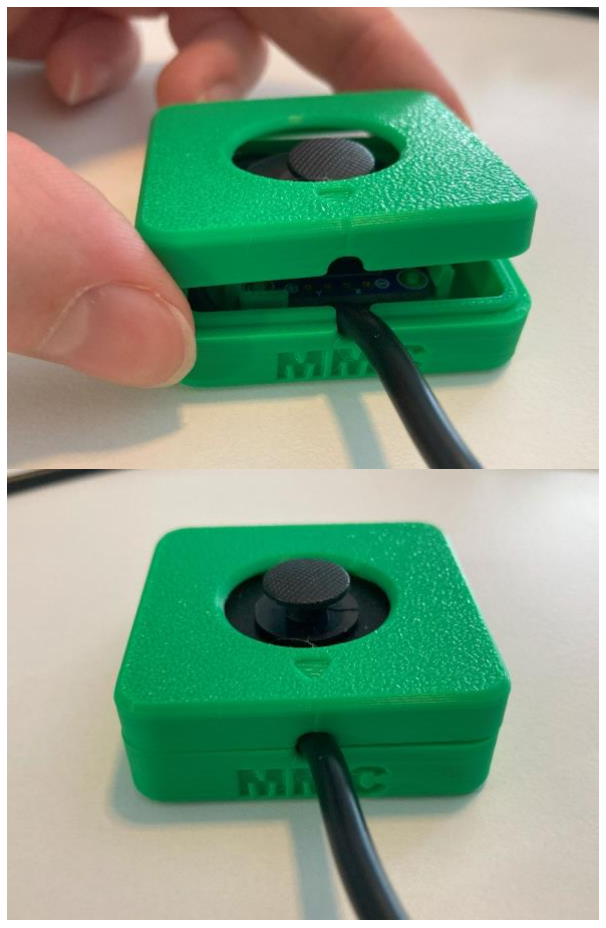
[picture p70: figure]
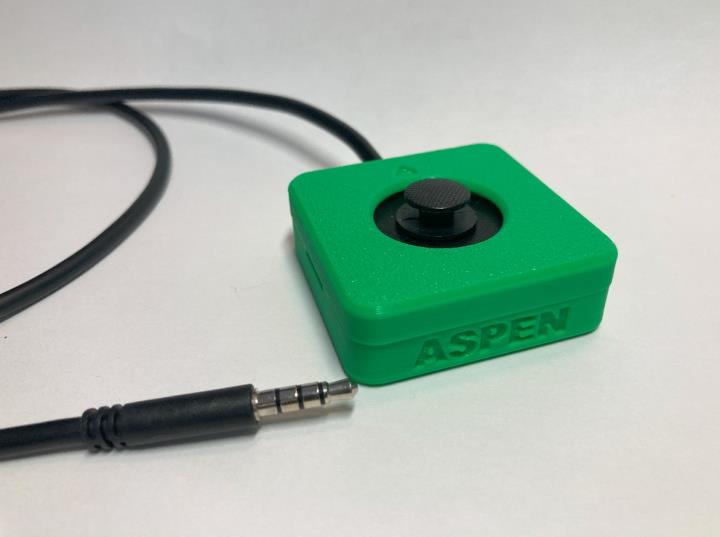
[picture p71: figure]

Files available at https://github.com/makersmakingchange/Aspen-Sliding-Joystick | Page 17 of 25
Step 11: Assemble Enclosure

Take the enclosure top, and with the cable indent away from you, aligned with the cable exit, place the top on the enclosure bottom and press down to snap into place.

Step 13: Joystick Assembly Complete The joystick assembly is now complete.

## MAKER GUIDE

Files available at https://github.com/makersmakingchange/Aspen-Sliding-Joystick | Page 18 of 25

### Testing

Now that you have your completed Aspen Joystick, you must test to make sure it is wired and assembled correctly. This can be done with a multimeter, or by plugging the joystick into one of the following: Forest Hub, Xbox Adaptive Controller (XAC), PlayStation Access Controller, Enabled Controller Mini, Enabled Controller, or other USB-HID controller that accepts the input of an analog joystick and connecting to a computer.

Testing using a Multimeter
A multimeter can be used to test if the wires are connected and soldered correctly. It is most important to ensure that there is no short circuit between the Sleeve (Ground) and Tip (Voltage), as this can damage the host device. It can be tricky to place the probes and move the joystick, so tape, or a second person can be helpful here.

Note: The intended joystick for this build has two 10 KΩ potentiometers, but some joysticks use 5 KΩ potentiometers, which will result in the expected multimeter readings to be halved

Test 1: Testing for Short Circuits
1. Set the multimeter to measure resistance in the 1-
10 KΩ range.
2. Hold the tip of the red probe of the multimeter to the Sleeve (Voltage) of the TRRS cable.
3. Hold the tip of the black probe of the multimeter to Ring 2 (Ground) on the TRRS cable.
4. Confirm that the resistance is between 4 – 6 KΩ.
a. Between 4 – 6 KΩ: No shorts. Proceed to next test.
b. Less than 50 Ω: There is a short circuit between a Ground and Voltage pin. This must be fixed to prevent damaging a host device. Open the joystick and review/fix your soldering joints.
c. Other values: There is a wiring problem. Open the joystick and review/fix your soldering joints.

If you have no short circuits, you can move on to testing the joystick directions. This can be done with either the multimeter, or with a USB-HID gamepad that accepts an analog joystick.

## MAKER GUIDE

Files available at https://github.com/makersmakingchange/Aspen-Sliding-Joystick | Page 19 of 25

Test 2: Testing Vertical Joystick Axis
1. Hold the tip of the red probe of the multimeter to the Sleeve (Voltage) of the TRRS cable.
2. Hold the tip of the black probe to Ring 1 (Y-axis) on the TRRS cable.
3. While holding the multimeter probes in place, move the joystick fully in the UP ↑ direction.
a. You may require a second person to hold the probes in place or move the joystick.
b. Otherwise, the joystick can be held in place with some tape to leave your hands free to hold the multimeter probes in place.
4. Read the resistance on the multimeter:
a. Less than .10 KΩ: The Y-axis potentiometer is wired correctly.
b. Otherwise, review the wiring diagram and ensure your wiring matches.
5. Release the joystick back to neutral position.

Test 3: Testing Horizontal Joystick Axis
1. Hold the tip of the red probe of the multimeter to the Sleeve (Voltage) of the TRRS cable.
2. Hold the tip of the black probe to Tip (X-axis) of the TRRS cable.
3. While holding the multimeter probes in place, move the joystick fully in the RIGHT → direction.
a. You may require a second person to hold the probes in place or move the joystick.
b. Otherwise, the joystick can be held in place with some tape to leave your hands free to hold the multimeter probes in place.
4. Read the resistance on the multimeter.
a. Less than .10 KΩ: The X-axis potentiometer is wired correctly.
a. Otherwise, review the wiring diagram and ensure your wiring matches.
5. Release the joystick back to neutral position.

## MAKER GUIDE

Files available at https://github.com/makersmakingchange/Aspen-Sliding-Joystick | Page 20 of 25

Troubleshooting
If tests 2 or 3 fail, here are the likely scenarios to address.

Test 2 Fail
If the multimeter reading increases instead of decreasing when moving the joystick from the neutral position to the UP direction, then the Voltage and Ground pins are opposite and need to be swapped.

If the multimeter reading does not change, then the X and Y axis pins are opposite and need to be swapped.

Test 3 fail
If the multimeter reading instead of decreasing when moving the joystick from the neutral position the RIGHT direction, then the Voltage and Ground pins are opposite and need to be swapped.

If the multimeter reading does not change, then the X and Y axis pins are opposite and need to be swapped.

Testing using an USB-HID Gamepad Interface Device
Before plugging the joystick into a USB-HID Gamepad Interface Device, ensure that there is no short circuit between the Tip and the Sleeve.
1. Plug the joystick into the analog joystick input for the host device.
a) X1 or X2 on an Xbox Adaptive Controller.
2. Plug the host device into a computer.
3. If using Windows, open “Set up USB Game Controllers” from the Control Panel. You can find this by searching your computer in the search bar next to the Windows icon.
a) If using a Mac, use https://hardwaretester.com/gamepad
4. Select the host device from the list of controllers and go to “Properties”.
5. Move your joystick and observe the movement of the cross hatch in the “Axes” window. Ensure it moves in the proper directions when you move the joystick (the arrow points in the up direction). If not, open the joystick and check your connections.

## MAKER GUIDE

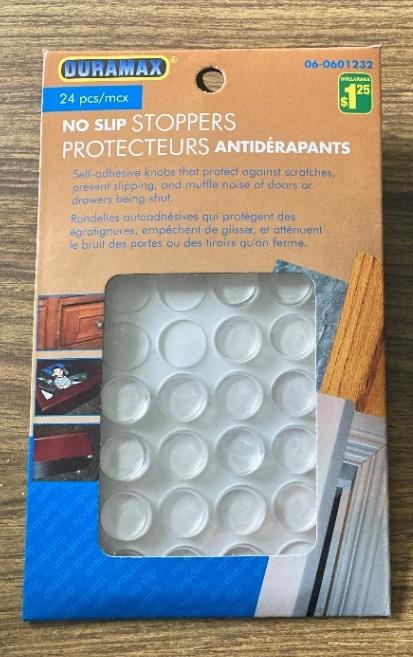
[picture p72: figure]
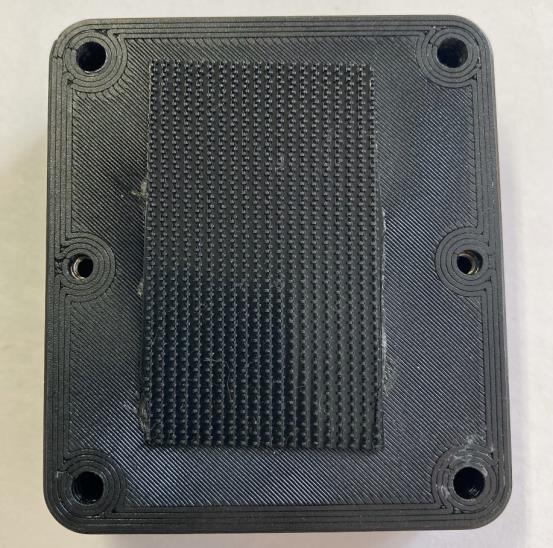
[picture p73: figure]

Files available at https://github.com/makersmakingchange/Aspen-Sliding-Joystick | Page 21 of 25

### Optional – Mounting

Table Top Mounting – Non-Slip Pads If using the joystick on a tabletop, and height of
the joystick is not a
concern, nonslip pads can
be added in each of the
four corners on the
bottom, as shown.

Table Top Mounting – Hook and Loop Fastener If using the joystick on a
tabletop or other surface
with hook and loop
fasteners, such as Velcro, stick the hook side (rough side) to the joystick and the loop side (soft side) to the surface to mount to.

## MAKER GUIDE

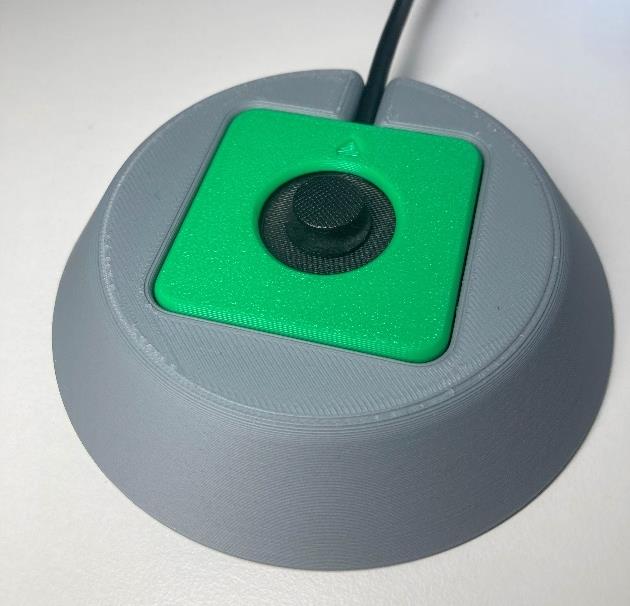
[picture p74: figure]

Files available at https://github.com/makersmakingchange/Aspen-Sliding-Joystick | Page 22 of 25

Table Top Mounting – Aspen Hand Support
To mount the joystick on a tabletop with added size for the user to support their hand, and optional non-slip pads on the bottom, the Aspen Hand Support can be used.
Step 1: (Optional) Add non slip pads
If desired, turn the 3D print for the hand support upside down, and add 4 optional non slip pads into the larger circular indents. You may want to add a dap of super glue for added security.
Step 2: Insert the Aspen Sliding Joystick into the hand support.
With the hand support right side up, place the Aspen Sliding Joystick into the hand support with the cable going out the cable slot, and with the joystick facing up.

## MAKER GUIDE

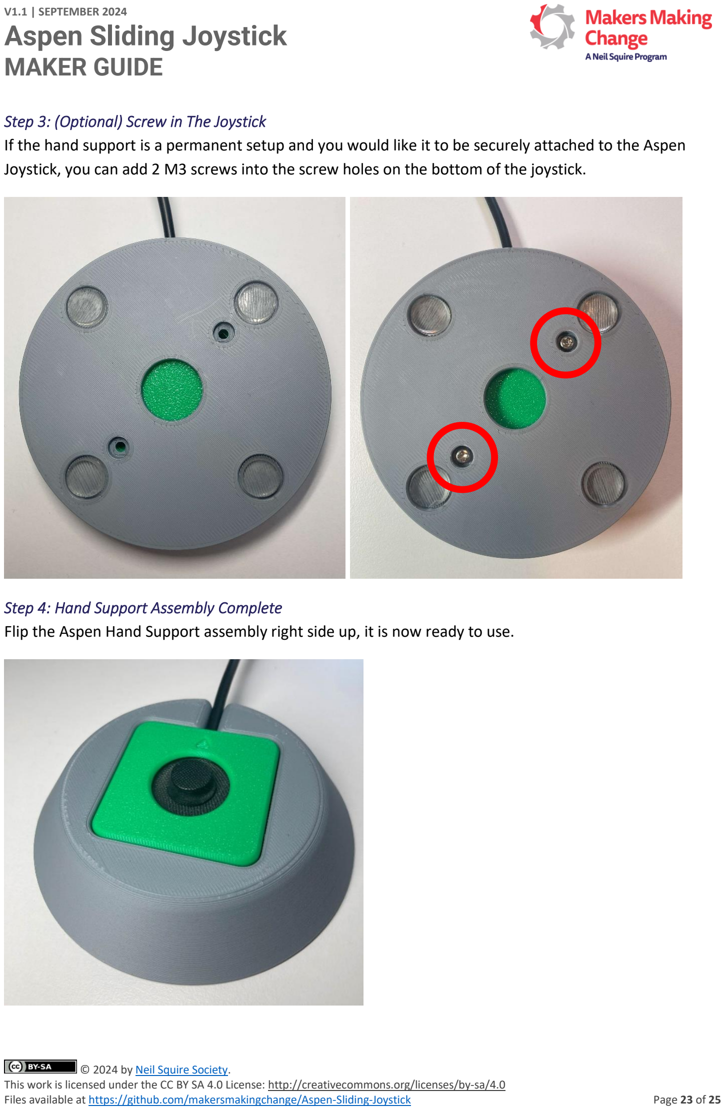
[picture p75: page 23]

Files available at https://github.com/makersmakingchange/Aspen-Sliding-Joystick | Page 23 of 25
Step 3: (Optional) Screw in The Joystick
If the hand support is a permanent setup and you would like it to be securely attached to the Aspen Joystick, you can add 2 M3 screws into the screw holes on the bottom of the joystick.
Step 4: Hand Support Assembly Complete
Flip the Aspen Hand Support assembly right side up, it is now ready to use.

## MAKER GUIDE

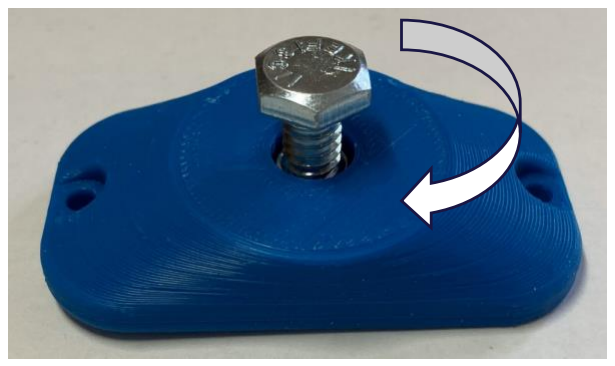
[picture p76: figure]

Files available at https://github.com/makersmakingchange/Aspen-Sliding-Joystick | Page 24 of 25

Camera Mount
To mount the joystick on a camera mount, the optional Joystick Camera Mount Adapter can be used.
Step 1: Prepare and Orient 3D Print

Flip the camera mount adapter around to reveal the recess with small slots.

Ensure all supports are removed from the 3D print.

Step 2: Insert Tee Nut

Insert the tee nut, lining up the barbs with the small slots in the 3D print.

Step 3: Screw in Bolt

Flip the part around and screw in a ¼-20 hex bolt.

## MAKER GUIDE

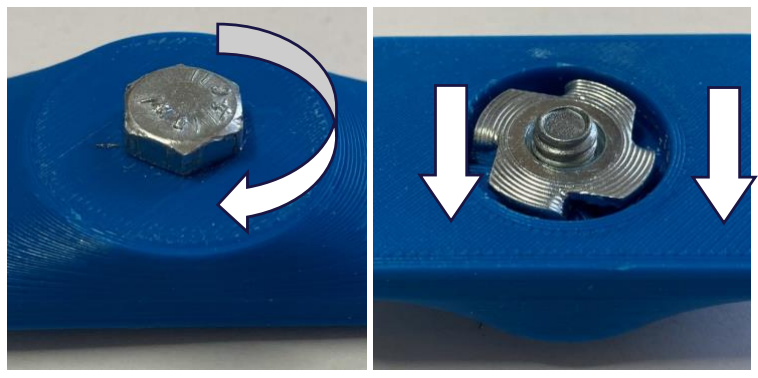
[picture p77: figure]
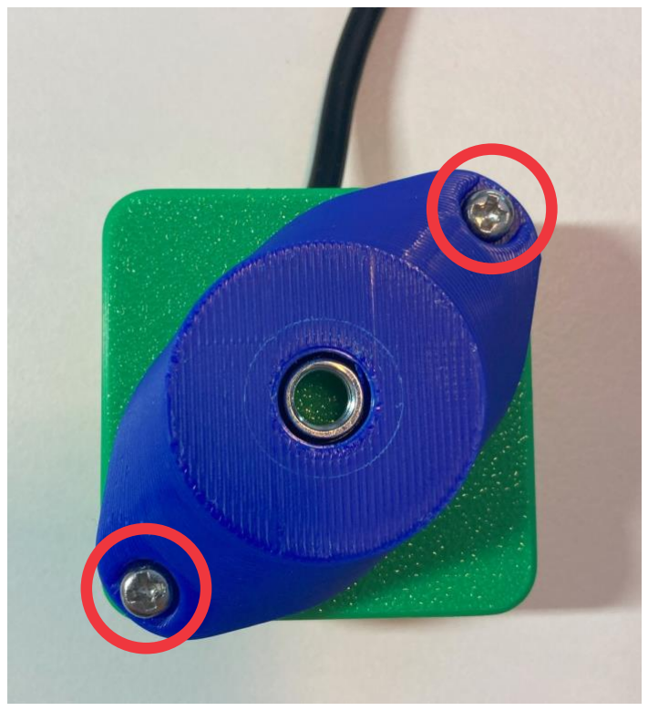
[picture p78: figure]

Files available at https://github.com/makersmakingchange/Aspen-Sliding-Joystick | Page 25 of 25
Step 4: Tighten Bolt

Tighten the bolt until the tee nut is seated down as far as possible.

(Alternatively, if you do not have acces to a bolt, the tee nut may be press fit as long as it sits flush with the 3D print.)

Step 5: Attach to Joystick

Using 2 M3 screws, screw the camera mount adapter to the bottom of the joystick in the two middle holes.

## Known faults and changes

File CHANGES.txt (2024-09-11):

------ASPEN SLIDING JOYSTICK------
            Changelog             
==================================

Version 1.1 	Date 09/11/2024
 - Added Aspen Hand Support (build file and design file)
 - Added the Aspen Hand Support to the Maker Guide, User Guide, Design Rationale, and BOM
 - Added photos of the Aspen in the Hand Support to the photos folder

Version 1.0 	Date 06/21/2024
 - Initial commit
 - Aspen Sliding Joystick design with supporting documentation
 - 5 Sliding Joystick toppers and 2 optional mount adapters (camera mount and RAM mount)
 - Design based on and adapted from the Birch Mini Joystick - A design, using the same joystick module
